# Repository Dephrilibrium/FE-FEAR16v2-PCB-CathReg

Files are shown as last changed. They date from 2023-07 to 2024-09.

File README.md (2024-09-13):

# FEAR-Cathode Regulation
This repository contains the KiCAD-design files for a shield of the F(ield) E(mission) A(rray) R(egulation) current control circuit.

Note: This project is part of the SubModule-repository [FE-FEAR16v2][FE-FEAR16v2-SubmoduleRepo], where you can find sub-repositories for other shield-PCBs, mainboard-PCB and the firmware.

# Description
The name "cathode regulation" comes from the original main purpose of regulating the potential (extraction voltage) of a field emission array (FEA = cathode) based on the current through this cathode. However, it can be used for all purposes where a potential needs to be regulation based on the current-flow through the device under test. During active regulation this shield acts like a current-source/-sink.

- The shield itself takes 1 DAC-output voltage (V~Ctrl~ = 0..10V) to adjust the current control.
- The A(mperemeter) is actually a shunt-resistor which defines the measurable current range. A 1MΩ for instance yields a range from 0.31 nA (resolution) to 10 µA, whereby its wisely to keep the current slightly below as 10 µA is the absolute maximum measurable value.
- The V(oltmeter) measures the internal voltage-drop over the FET.

Note: Both, A and V use potentiometers to adjust their feedback-loop amplification. Due to tolerances on all the parts, its recommended to use a shield only at a specific mainboard and a specific channel-position at which the boards were calibrated.

**Principle of the cathode regulation:**
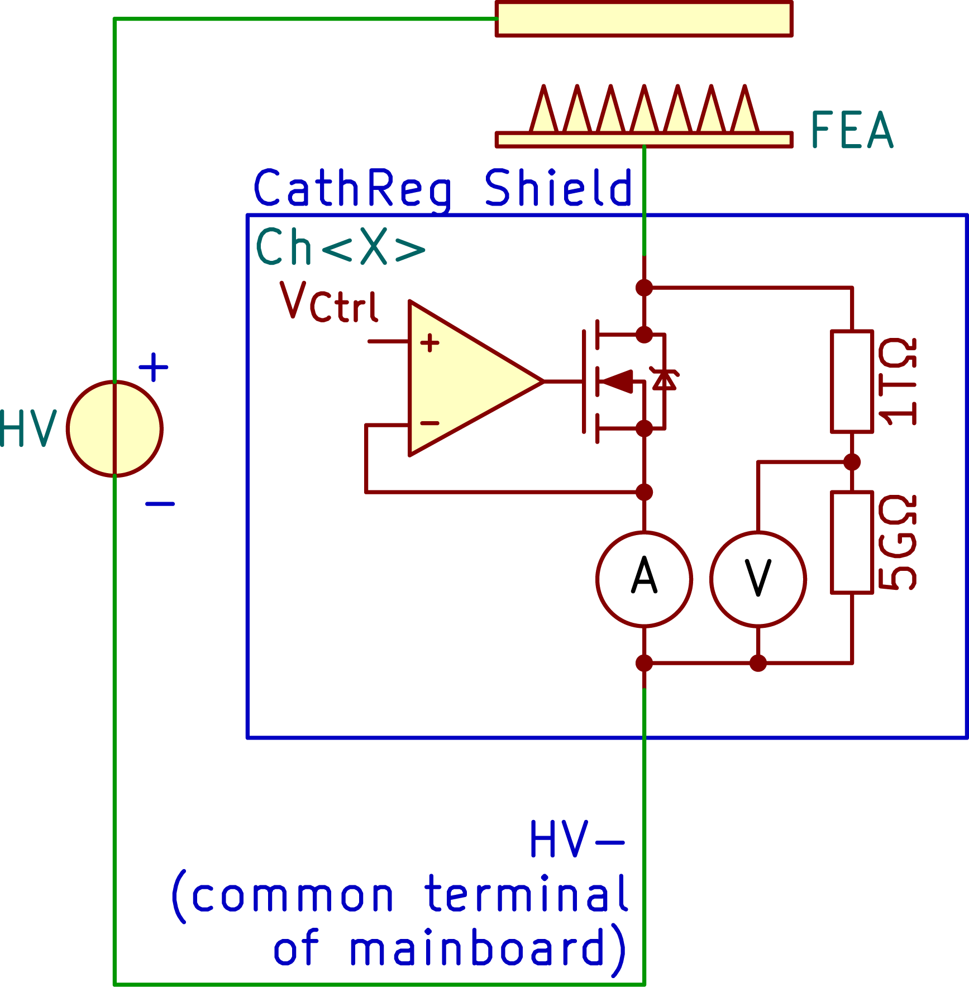
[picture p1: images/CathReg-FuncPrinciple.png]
Principle of the regulation


# HowTo to connect (samples and for calibration)
1. Place a shield on a mainboard/channel-slot.
2. Calibration: continue with step 3.), otherwise go to 6.)

3. Connect the positive supply of the high-voltage source to the FEA-input (see figure above) and the negative supply (GND) to the HV- input. For a fine calibration, add an amperemeter in series.

    1. Apply a high voltage to the input (e.g. 1kV) and define a V~Ctrl~ (e.g. 9V).

4. Calibrate V~Shnt~
    1. Adjust the current gain potentiometer, so that the measured ADC value divided by the shunt-resistance is equal to the amperemeter-value (V~Shnt~/R~Shunt~ = I~Amperemeter~)

5. Calibrate V~Drp~
    1. Adjust the voltage-drop gain potentiometer. The board projects a voltage range of &pm;1500V into a range of &pm;10V using a voltage divider with huge resistance values. Example for positive voltage:
    1500V * 5GΩ / 1005GΩ * Gain = 7.462..V * Gain = 10V
    Gain = 10V / 7.462..V = 1.34

6. Connect FEA on the shield's screw terminal and the most negative supply to to HV- (which is the mainboard's common-terminal).

Note: The FEAR command-documentation can be found in the firmware-repository (see [FE-FEAR16v2 Submodule-Repo][FE-FEAR16v2-SubmoduleRepo]).

[FE-FEAR16v2-SubmoduleRepo]: https://github.com/Dephrilibrium/FE-FEAR16v2

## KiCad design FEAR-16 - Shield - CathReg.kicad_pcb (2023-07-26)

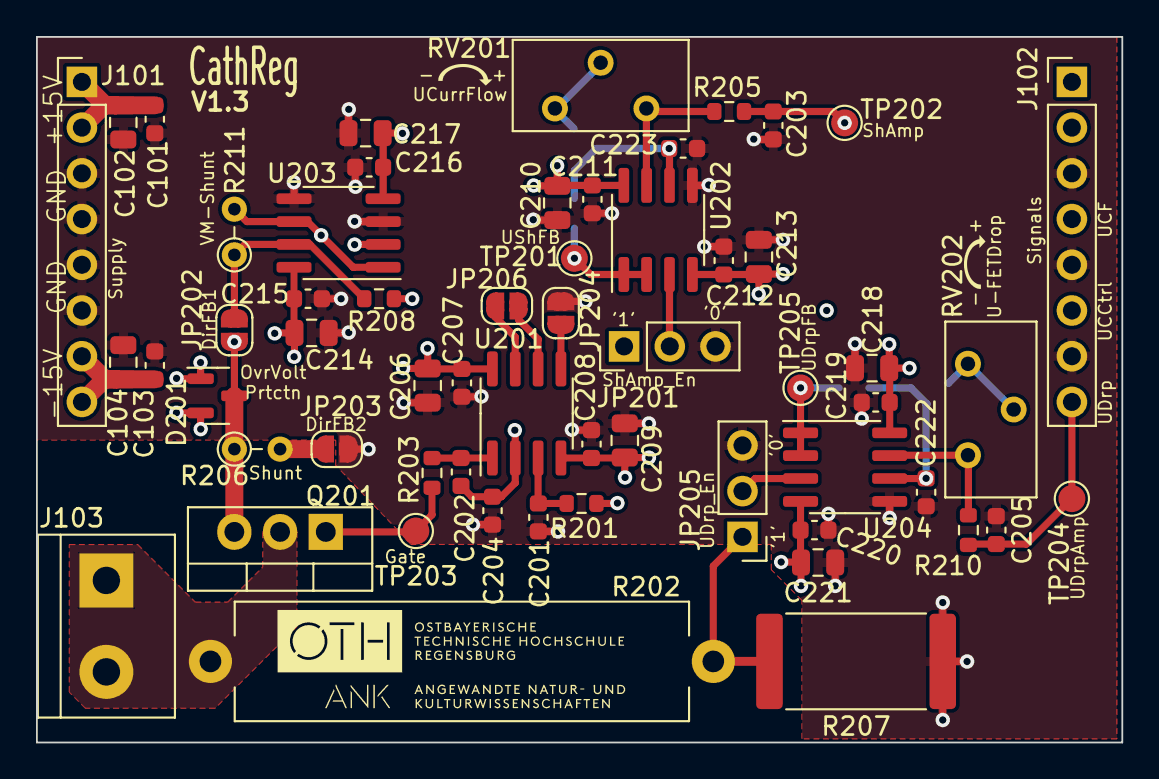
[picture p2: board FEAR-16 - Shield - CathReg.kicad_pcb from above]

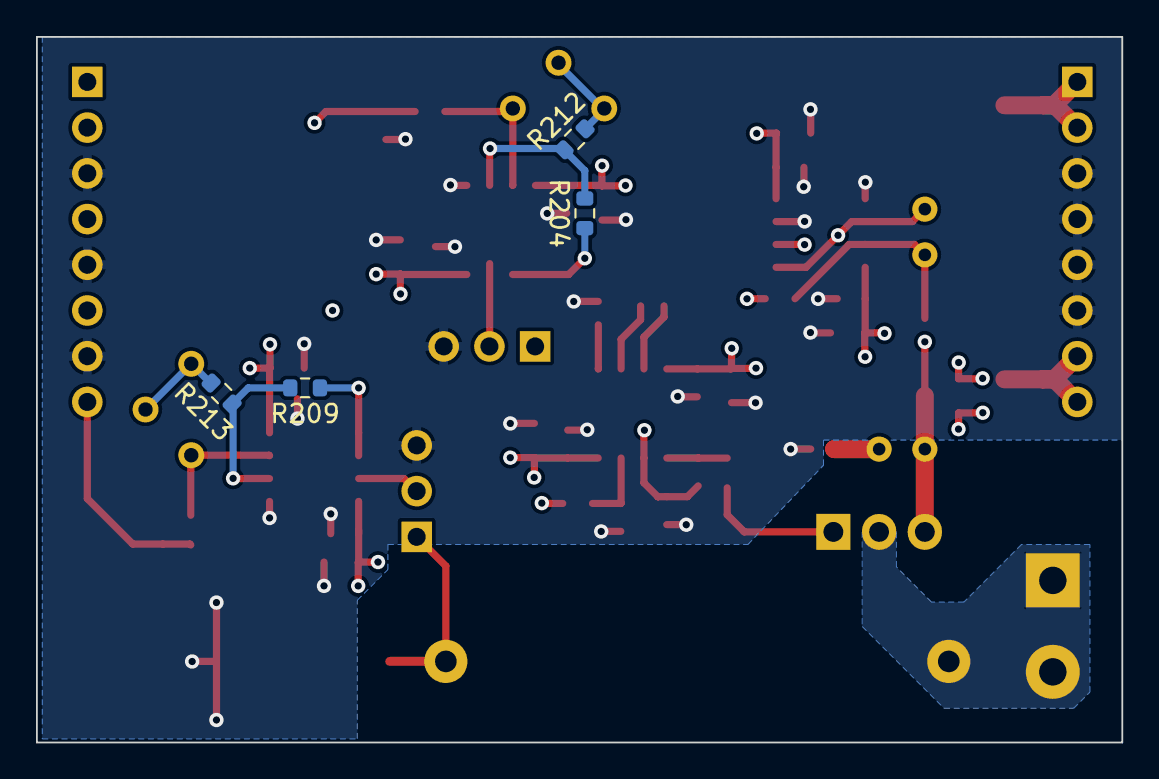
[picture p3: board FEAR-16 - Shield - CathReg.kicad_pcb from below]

Board: 4 copper layers, 60.3 x 39.2 mm, 62 parts (4 on the bottom side), 28 nets.

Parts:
C101, C103, C202, C207, C208, C211, C212, C215, C216, C219, C220: 100n/25V; C_0603_1608Metric
C102, C104, C206, C209, C210, C213, C214, C217, C218, C221: 10µ/25V; C_0805_2012Metric
C201: 1n/25V; C_0603_1608Metric
C203, C205: 470p/25V; C_0603_1608Metric
C204: 1n/25V (opt.); C_0603_1608Metric
C222, C223: 220n/25V; C_0603_1608Metric
D201: BAV99; SOT-23
J101: Supply; PinHeader_1x08_P2.54mm_Vertical
J102: Signals; PinHeader_1x08_P2.54mm_Vertical
J103: Channel-In; TerminalBlock_bornier-2_P5.08mm
JP201: ShAmp_En; PinHeader_1x03_P2.54mm_Vertical
JP202: DirFB1; SolderJumper-2_P1.3mm_Open_RoundedPad1.0x1.5mm
JP203: DirFB2; SolderJumper-2_P1.3mm_Open_RoundedPad1.0x1.5mm
JP204: ResGND; SolderJumper-2_P1.3mm_Open_RoundedPad1.0x1.5mm
JP205: UDrp_En; PinHeader_1x03_P2.54mm_Vertical
JP206: FedLp; SolderJumper-2_P1.3mm_Open_RoundedPad1.0x1.5mm
Q201: NDFPD1N150CG; TO-220-3_Vertical
R201: 1k; R_0603_1608Metric
R202: 1T/5%; R_Axial_Power_L25.0mm_W6.4mm_P27.94mm
R203: 220R; R_0603_1608Metric
R204, R205, R209, R210, R212, R213: 100k; R_0603_1608Metric
R206: Shunt; R_Axial_DIN0204_L3.6mm_D1.6mm_P2.54mm_Vertical
R207: 5G/5%; R_4020_10251Metric
R208: 220R (opt); R_0603_1608Metric
R211: VM-Shunt; R_Axial_DIN0204_L3.6mm_D1.6mm_P2.54mm_Vertical
RV201, RV202: 50k; Potentiometer_Bourns_3296Y_Vertical
TP201: UShFB; TestPoint_Pad_D1.5mm
TP202: ShAmp; TestPoint_Pad_D1.5mm
TP203: Gate; TestPoint_Pad_D1.5mm
TP204: UDrpAmp; TestPoint_Pad_D1.5mm
TP205: UDrpFB; TestPoint_Pad_D1.5mm
U201, U202, U203, U204: OPA2156xD; SOIC-8_3.9x4.9mm_P1.27mm

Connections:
+15V: C101.2, C102.2, C206.2, C207.2, C210.2, C211.2, C214.2, C215.2, C218.2, C219.2, D201.2 (A), J101.1, J101.2, U201.8 (V+), U202.8 (V+), U203.8 (V+), U204.8 (V+)
-15V: C103.1, C104.1, C208.2, C209.2, C212.2, C213.2, C216.2, C217.2, C220.2, C221.2, D201.1 (K), J101.7, J101.8, U201.4 (V-), U202.4 (V-), U203.4 (V-), U204.4 (V-)
/ChIn: J103.1, J103.2, Q201.2 (D), R202.2
/Channel/UDrp: JP205.1 (A), R202.1, R207.2
/Channel/USh: C202.1, C204.2, JP201.1 (A), R208.2, U201.2 (-)
/UCurrCtrl: J102.6, R201.1
/UCurrFlow: C203.2, J102.4, R205.1, TP202.1
/UFETDrop: C205.2, J102.8, R210.1, TP204.1
GND: C101.1, C102.1, C103.2, C104.2, C201.2, C203.1, C204.1, C205.1, C206.1, C207.1, C208.1, C209.1, C210.1, C211.1, C212.1, C213.1, C214.1, C215.1, C216.1, C217.1, C218.1, C219.1, C220.1, C221.1, C222.1, C223.1, J101.3, J101.4, J101.5, J101.6, J102.3, J102.5, J102.7, JP201.3 (B), JP203.2 (B), JP204.1 (A), JP205.3 (B), R207.1, U202.5 (+), U203.3 (+), U203.5 (+), U204.5 (+)
unnamed: C202.2, R203.1, U201.1
unnamed: JP201.2 (C), U202.3 (+)
unnamed: JP202.1 (A), R208.1, R211.1, U203.7
unnamed: D201.3 (K), JP202.2 (B), Q201.3 (S), R206.1, U203.2 (-)
unnamed: JP203.1 (A), R206.2, R211.2, U203.1, U203.6 (-)
unnamed: JP204.2 (B), U201.5 (+)
unnamed: JP205.2 (C), U204.3 (+)
unnamed: JP206.1 (A), U201.7
unnamed: JP206.2 (B), U201.6 (-)
unnamed: Q201.1 (G), R203.2, TP203.1
unnamed: R205.2, RV201.3, U202.7
unnamed: R210.2, RV202.3, U204.7
unnamed: R212.2, RV201.1, RV201.2
unnamed: R213.2, RV202.1, RV202.2
unnamed: C201.1, R201.2, U201.3 (+)
unnamed: R204.1, TP201.1, U202.1, U202.2 (-)
unnamed: C223.2, R204.2, R212.1, U202.6 (-)
unnamed: R209.1, TP205.1, U204.1, U204.2 (-)
unnamed: C222.2, R209.2, R213.1, U204.6 (-)

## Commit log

2023-07-20 V1.3 (improved fine-tuning of CF- and UD-Amps)
    PCB Changes:
    - Amplification Poti (1Meg) changed to Offset-Resistor (100k) + Poti (50k) to achieve 20x finer tuning of the amplification
    Misc.:
    - Fixed .gitignore to ignore the prl files
    [FEAR-16 - Shield - CathReg.kicad_pcb, FEAR-16 - Shield - CathReg.kicad_sch, OneChannel.kicad_sch]
2023-07-26 Added offset resistor in row to poti for finer tuning of the measurement amplification
    [FEAR-16 - Shield - CathReg.kicad_pcb]
2023-09-01 Specified resistor and poti with the values of the buyed ones
    [OneChannel.kicad_sch]
2024-06-11 Removed C202 and adjusted .gitignore
    - Added new temporary files to .gitignore
    - C202 is not applicable for this circuit and was removed (now an optional part)
    - Now using KiCAD 8 (new Project, Board, Schematic files mostly change a bit)
    [FEAR-16 - Shield - CathReg.kicad_sch, OneChannel.kicad_sch]
2024-09-12 Added comments on the UDrp feedback-loop
    [OneChannel.kicad_sch]
